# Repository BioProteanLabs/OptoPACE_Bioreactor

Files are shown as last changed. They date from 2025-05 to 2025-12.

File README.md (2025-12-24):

# OptoPACE_Bioreactor

## The OptoPACE Bioreactor (OPB): An Accessible Turbidostat System with Phage-Assisted Continuous Evolution Capability and Optogenetic Controls

## Authors
1. Crane, Ryan D.* 
2. Isaacs, William T.*
3. Ijaz, Manal*
4. Salazar, Nicole
5. Botello, Brianna
6. Kim, Michelle
7. Gonani, Kaeden W.
8. Flores-Mora, Fernando E.
9. Bartelle, Benjamin B.

*co-first

## Abstract:
Continuous culture systems are essential for synthetic biology techniques like Directed Evolution (DE) and Phage-Assisted Continuous Evolution (PACE), which require metabolically active bacterial cultures for extended periods. Turbidostats, which maintain cell density using real-time optical density (OD) feedback, offer ideal conditions for inducing gene expression during mid-log phase, which is the optimal growth stage for synthetic circuit activity. However, current PACE-compatible bioreactors are either cost-prohibitive or require significant technical expertise. Here, we present the OptoPACE Bioreactor (OPB), a low-cost, user-friendly turbidostat system optimized for PACE and optogenetic control. The OPB uses a 650 nm laser and photoresistor to measure turbidity, an Arduino microcontroller for feedback control, and NeoPixel LEDs to enable multispectral optogenetic stimulation. Designed with 3D-printed components and off-the-shelf electronics, the system operates with a single peristaltic pump and uses the siphon effect to simplify fluidics. A custom motor control shield and an LCD-rotary encoder interface enable code-free operation. The OPB supports dual bioreactors connected unidirectionally, ensuring continuous culture while maintaining precise control over optical inputs and nutrient flow. The entire system can be built for under $200, significantly lowering the barrier to entry for labs interested in continuous evolution. By combining affordability, modularity, and ease of use, the OptoPACE Bioreactor provides a robust platform for protein engineering and synthetic biology, enabling broader adoption of advanced continuous evolution methods like PACE.

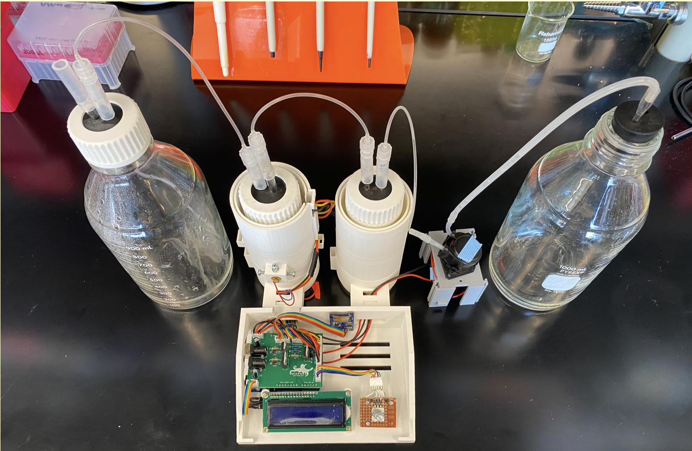
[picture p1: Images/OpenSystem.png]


## Metadata Overview:
Main design files: https://github.com/BioProteanLabs/OptoPACE_Bioreactor/tree/main
Target group: undergraduate researchers, under-resourced laboratories in synthetic biology, students interested in biological hardware
Skills required: 3d printing - easy; software implementation - easy; physical assembly - intermediate; electrical assembly - advanced

Continuous bacterial culture bioreactors are widely employed in biological research, with recent applications in the directed evolution (DE) of biomolecules [1, 3]. In a typical DE experiment, bioreactors  maintain a population of microorganisms in a metabolically active state to support growth and expression of synthetic biological programs. For methods like phage assisted continuous evolution (PACE), two tandem bioreactors are needed: one for growing a substrate culture that feeds into a second “lagoon” to support bacteriophages actively evolving. 
For PACE, maintaining the substrate culture at a steady state gives consistent conditions for DE, requiring either a chemostat or turbidostat control system. Chemostat bioreactors are simpler in that they supply a steady state of nutrients, while a turbidostat makes continual adjustments based on feedback—namely, culture density or turbidity [8, 9, 17]. Turbidostats allow for more optimal and customizable culture conditions but require continual monitoring and control hardware for adjustments based on feedback.
Turbidity is typically measured by optical density (OD), which reflects both light absorption by molecules in the culture, such as pigments, and light scattering from materials with different refractive indexes, typically cell membrane lipids. OD serves as a real-time quantitative assay of cell concentration, allowing researchers to infer the growth stage of the bacterial population. In a bacterial culture, OD measurements typically begin with exponential growth, reach mid-log phase, and eventually flatten out into “death phase” as resources become limited. For the production of recombinant proteins at experimental and industrial scales, mid-log phase is considered the optimal state for inducing protein expression or a synthetic biological program. In a turbidostat bioreactor, continuous monitoring of bacterial growth allows users to identify the mid-log phase, input nutrients to maintain this optimal point, and induce expression of biological circuits.
Induction of biological circuits presents another layer of control required in a bioreactor. Historically, this has meant adding specific sugars or their chemical analog to regulate bacterial operons to initiate expression [2, 16]. This requires an additional chemostat input for the induction agent. More recently, optogenetic circuits—based on biology from plants and cyanobacteria—allow for the induction of gene expression using light. Current developments in synthetic biology have even enabled wavelength-specific optogenetic circuits. With stable culture conditions and multiple biological control inputs, bioreactors could control several genetic circuits simultaneously [4, 10, 11, 14].
Despite their potential, experimental-scale turbidostat bioreactors are not commonly available. The literature indicates that establishing a functional PACE workflow often requires years of effort due to the dual challenges of designing effective synthetic biological circuits and building reliable hardware to support culture [12, 13]. Additional obstacles—such as extensive setup time and the need for frequent maintenance due to microbial biofilm accumulation on culture surfaces—make developing an automated PACE workflow even more difficult to implement.

**The OptoPACE Bioreactor is designed for optogenetic control of synthetic biological circuits.**
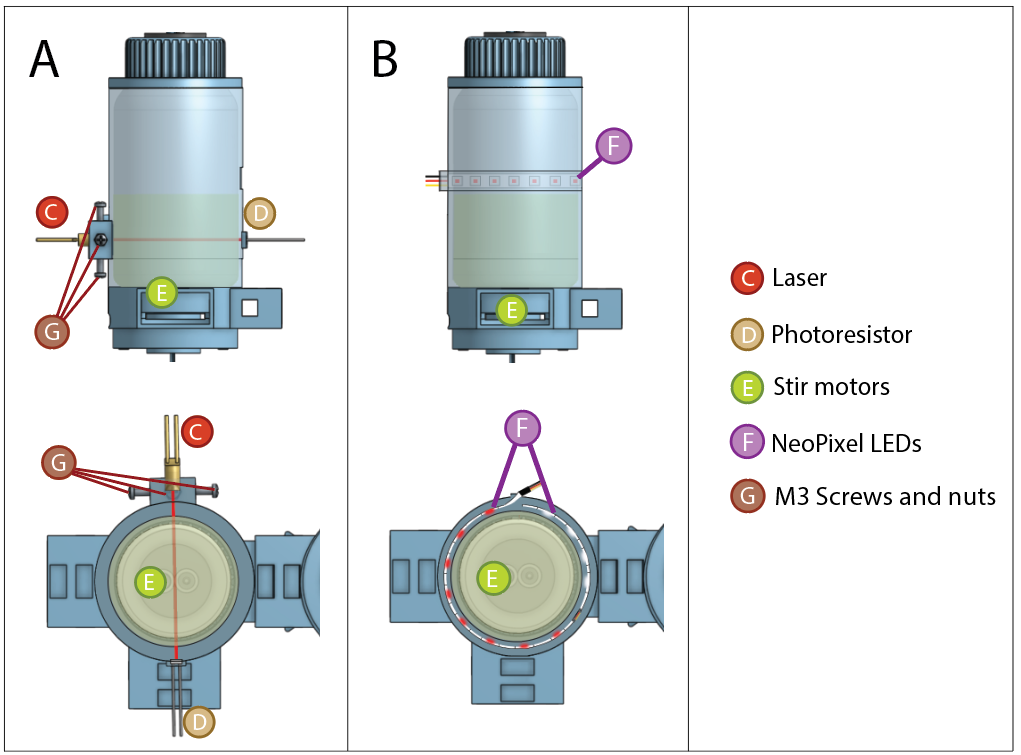
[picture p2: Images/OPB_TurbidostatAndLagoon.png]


**The OptoPACE Bioreactor uses the siphon effect to minimize the number of pumps needed.**

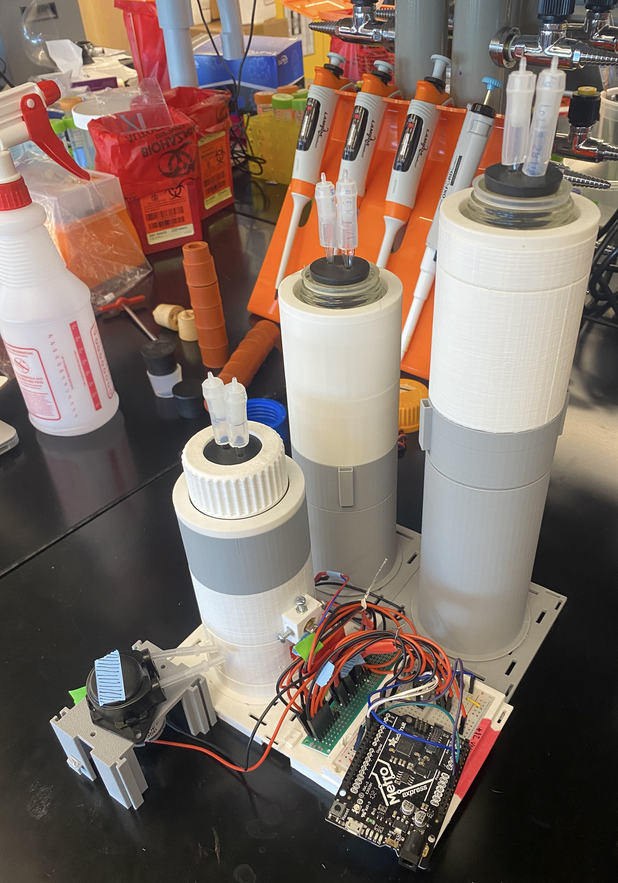
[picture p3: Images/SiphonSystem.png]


**The OptoPACE Bioreactor is controlled by a single Arduino microcontroller and a custom designed motor control shield. It uses a 650nm laser and a photoresistor to measure turbidity, and NeoPixel LEDs for multispectral control.**

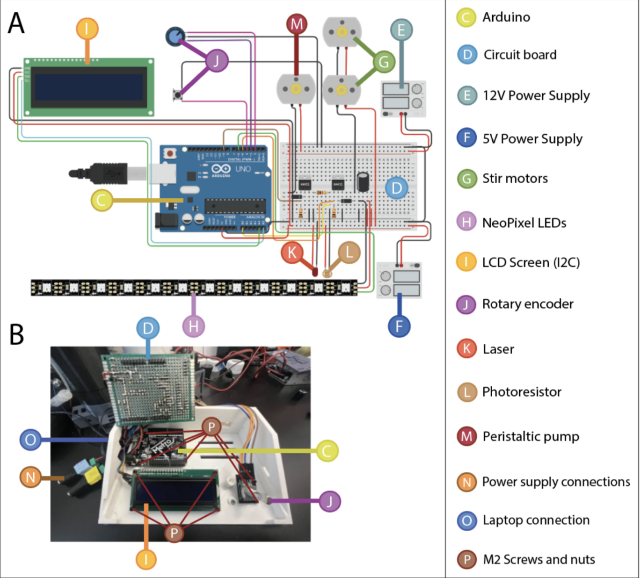
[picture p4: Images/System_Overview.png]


**The OptoPACE Bioreactor uses an LCD screen and rotary encoder as an interface.**
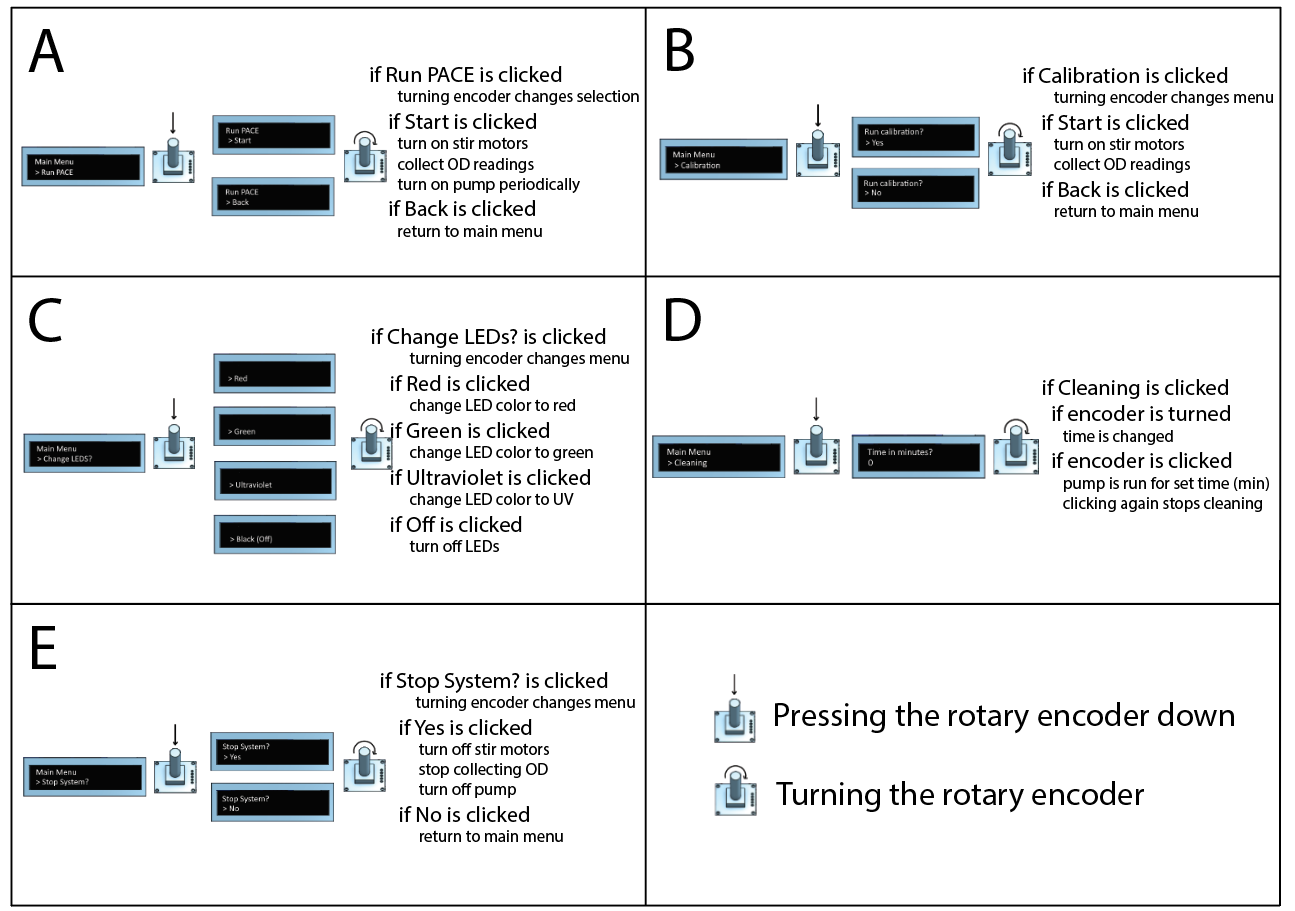
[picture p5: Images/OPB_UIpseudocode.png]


**Turbidity measurements from a 20 hour continuous run.**
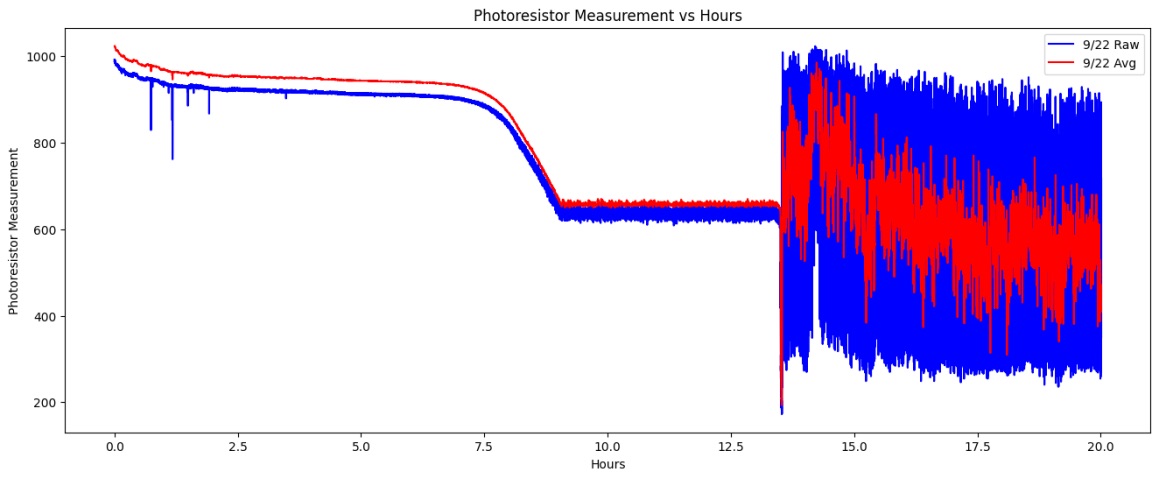
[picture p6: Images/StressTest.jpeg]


 Early measurements required an hour to stabilize before giving consistent readings. Turbidity set point was 650, which was achieved after 9 hours of culture. The turbidostat was maintained for the next 4 hours before the media bottle ran out, giving high noise readings as air bubbles were introduced from the empty line.

## References
[1]	*K. M. Esvelt, J. C. Carlson, and D. R. Liu, “A System for the Continuous Directed Evolution of Biomolecules,” Nature, vol. 472, no. 7344, pp. 499–503, Apr. 2011, doi: 10.1038/nature09929.*

[2]*A. H. Badran and D. R. Liu, “In vivo continuous directed evolution,” Current Opinion in Chemical Biology, vol. 24, pp. 1–10, Feb. 2015, doi: 10.1016/j.cbpa.2014.09.040.*

[3]	*A. Novick and L. Szilard, “Description of the Chemostat,” Science, vol. 112, no. 2920, pp. 715–716, Dec. 1950, doi: 10.1126/science.112.2920.715.* 

[4]	*C. N. Takahashi, A. W. Miller, F. Ekness, M. J. Dunham, and E. Klavins, “A Low Cost, Customizable Turbidostat for Use in Synthetic Circuit Characterization,” ACS Synth Biol, vol. 4, no. 1, pp. 32–38, Jan. 2015, doi: 10.1021/sb500165g.* 

[5]	*A. M. McGeachy, Z. A. Meacham, and N. T. Ingolia, “An Accessible Continuous-Culture Turbidostat for Pooled Analysis of Complex Libraries,” ACS Synth. Biol., vol. 8, no. 4, pp. 844–856, Apr. 2019, doi: 10.1021/acssynbio.8b00529.* 

[6]	*J. De Baets, B. De Paepe, and M. De Mey, “Delaying production with prokaryotic inducible expression systems,” Microb Cell Fact, vol. 23, p. 249, Sept. 2024, doi: 10.1186/s12934-024-02523-w.*

[7]	*T. Sanganeria and B. Bordoni, “Genetics, Inducible Operon,” in StatPearls, Treasure Island (FL): StatPearls Publishing, 2025. Accessed: May 28, 2025. [Online]. Available: http://www.ncbi.nlm.nih.gov/books/NBK564361/* 

[8]	*R. Ohlendorf, R. R. Vidavski, A. Eldar, K. Moffat, and A. Möglich, “From Dusk till Dawn: One-Plasmid Systems for Light-Regulated Gene Expression,” Journal of Molecular Biology, vol. 416, no. 4, pp. 534–542, Mar. 2012, doi: 10.1016/j.jmb.2012.01.001.* 

[9]	*E. J. Olson, L. A. Hartsough, B. P. Landry, R. Shroff, and J. J. Tabor, “Characterizing bacterial gene circuit dynamics with optically programmed gene expression signals,” Nat Methods, vol. 11, no. 4, pp. 449–455, Apr. 2014, doi: 10.1038/nmeth.2884.* 

[10]*P. Ramakrishnan and J. J. Tabor, “Repurposing Synechocystis PCC6803 UirS–UirR as a UV-Violet/Green Photoreversible Transcriptional Regulatory Tool in E. coli,” ACS Synth. Biol., vol. 5, no. 7, pp. 733–740, July 2016, doi: 10.1021/acssynbio.6b00068.*

[11]*L. Forbes, M. Papanatsiou, A. Palombo, J. M. Christie, and A. Amtmann, “Optogenetic control of gene expression in the cyanobacterium Synechococcus sp. PCC 7002,” Front. Bioeng. Biotechnol., vol. 12, Jan. 2025, doi: 10.3389/fbioe.2024.1529022.* 

[12]*S. C. Popa, I. Inamoto, B. W. Thuronyi, and J. A. Shin, “Phage Assisted Continuous Evolution (PACE): A How-to Guide for Directed Evolution,” Nov. 2019, Accessed: Mar. 09, 2020. [Online]. Available: https://www.preprints.org/manuscript/201911.0040/v1*

[13]*S. C. Popa, I. Inamoto, B. W. Thuronyi, and J. A. Shin, “Phage-Assisted Continuous Evolution (PACE): A Guide Focused on Evolving Protein-DNA Interactions,” ACS Omega, vol. 5, no. 42, pp. 26957–26966, Oct. 2020, doi: 10.1021/acsomega.0c03508.* 

[14]*U. Riek, R. Tuerk, T. Wallimann, U. Schlattner, and D. Neumann, “An Automated Home-Built Low-Cost Fermenter Suitable for Large-Scale Bacterial Expression of Proteins in Escherichia Coli,” BioTechniques, vol. 45, no. 2, pp. 187–189, Aug. 2008, doi: 10.2144/000112830.* 

[15]*D. Matteau, V. Baby, S. Pelletier, and S. Rodrigue, “A Small-Volume, Low-Cost, and Versatile Continuous Culture Device,” PLOS ONE, vol. 10, no. 7, p. e0133384, July 2015, doi: 10.1371/journal.pone.0133384.*

[16]*B. G. Wong, C. P. Mancuso, S. Kiriakov, C. J. Bashor, and A. S. Khalil, “Precise, automated control of conditions for high-throughput growth of yeast and bacteria with eVOLVER,” Nat Biotechnol, vol. 36, no. 7, pp. 614–623, Aug. 2018, doi: 10.1038/nbt.4151.*

[17]*Z. J. Heins, C. P. Mancuso, S. Kiriakov, B. G. Wong, C. J. Bashor, and A. S. Khalil, “Designing Automated, High-throughput, Continuous Cell Growth Experiments Using eVOLVER,” J Vis Exp, no. 147, May 2019, doi: 10.3791/59652.* 

[18]*V. Gopalakrishnan et al., “A low-cost, open-source evolutionary bioreactor and its educational use,” Sept. 01, 2022, bioRxiv. doi: 10.1101/729434.*

##
Article: CC-BY 4.0. See: https://creativecommons.org/share-your-work/cclicenses/ 
Hardware: CERN-OHL-P Permissive. See: https://cern-ohl.web.cern.ch 
Software: MIT-0. See: https://opensource.org/license/mit-0

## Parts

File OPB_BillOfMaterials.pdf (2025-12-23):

Cost (total in USD) | Per unit (USD)

Quantity
Required | Link
Pumps:
Peristaltic Pump | 24.95 | 24.95 | 1 https://www.adafruit.com/product/1150

Electronics:
Arduino Uno | 16.99 | 16.99 | 1 https://www.amazon.com/ELEGOO-Board-ATmega328P-ATMEGA16U2-Compliant/dp/B01EWOE0UU/ref=sr_1_2?crid=2BH7CIKCJ7CFA&dib=eyJ2IjoiMSJ9.MazmhFfn-DF8W5oyX_S-tDFAqLRDaMJSkroaZhdQMdisBLxmXEqtvF1FOCIWCK9VmMcdLxz4TK_dkOFiN4Rs4G1MOHO0C2cdoznNzQO9fitpRigfG_jyAHAxld8StKFz9U3h0JzKR6nlSri_QrVfRveh9TLyUJtKpQYNyRvr7e_Mk90qR3Vuww9b6Qn0lZH-mpveGqZg1Tc_CPVMISl0SIQF9eqJeR12jGkVYwXVRCChSu2XjLfS69RXut5ycPQBIdoHiU0czHEM2wM81zCh5hcre4O_QuutMAEhb_OEpfc.n_AJTySz6zBJVmoDv2wWDHNbWEV4MwIe4viY1KqEE1s&dib_tag=se&keywords=arduino+uno&qid=1727481167&s=industrial&sprefix=arduino+uno%2Cindustrial%2C129&sr=1-2
DC Motors | 6.99 | 1.7475 | 2 https://www.amazon.com/BOJACK-Pcs-Type-130-EK1450/dp/B09FPXF1QK/ref=sr_1_5?crid=SYDPQHVU1UCJ&dib=eyJ2IjoiMSJ9.ZvsO9y9VV2Cti8BPB2elIcQrtpUiZfOZ90OiEF3u8S2JqaXfD8roBZbpWuHwGUnWUJrtgxDCdDbqlT062z_vzXDY4UDEtTG2QOMZvhHwkoVGQaoRdqJQJRGFWIuxLYeunvejxsyGBOZgrbz7kBY9varfIFxPFtSZM_t88NIoVAv9nuIoEJbI5mnzILcSL-YL2eq_LeHGlcL8qbhE7fut4_CdGq03AfdYGX6FPTGZ8sx3kr_MgYbUSgLNgBAUdTIr1PRMZQJKwQBsy-QLFd201Fft08rG1EnqHYplswOcBfA.tpAMfRI84GYtpn5l6mxYFQuOmqMq7r5aFAcDlF5maa0&dib_tag=se&keywords=dc+motor+arduino&qid=1727489473&sprefix=dc+motor+arduino%2Caps%2C138&sr=8-5
Magnet for Stir Bar | 1.5 | 0.75 | 2 https://www.kjmagnetics.com/proddetail.asp?prod=B22C
Neo Pixel RGB Strip (1
meter) | 16.95 | 4.97 | 1 https://www.adafruit.com/product/1426?gad_source=1&gclid=Cj0KCQjwsuSzBhCLARIsAIcdLm7B5-E9eEBKmAclRtZ55TevoP9Ts5JCG6-ikKHFX-0JpmEfh3KP4hUaAuzuEALw_wcB
Neo Pixel UV Strip (1
meter) | 19.95 | 4.92 | 1 https://www.adafruit.com/product/3851?gad_source=1&gclid=Cj0KCQjwsuSzBhCLARIsAIcdLm7sCD9aQWDhDVkyhXy79CN7jM51O9Vu0E5j3pv7IjfmdTo9FJND3uEaAuvcEALw_wcB
Capacitor | 6.99 | 0.466 | 1 https://www.amazon.com/ALLECIN-Electrolytic-Capacitor-0-2x0-43in-Capacitors/dp/B0CMQBXG8W/ref=sr_1_1_sspa?crid=2P6FQCTPPZET1&dib=eyJ2IjoiMSJ9.EeRzVxgbry73PU81OfEdUTHHxefg7__akg6enD1ug2QqvUMahZM0egv24Ncmgsr6QNtSmHqpcjtyXPLhjQ04OR9VbHoEDxix56ssPrgHx8krXzxMMxhvY6eJbWf1SYPKSs3Mp_k5pNcwe7tIE1zYPnX0hH0U6DMaMaYMbpqlf_Az75BOFh7WiRFcDC9D44D6rOJ_BwdmqKI-1jNOrCrLl_U50FppxQuiJycx_DZ-swbkCzMISijJE0fuztHdx1gDlNp8sfdWhomQoorPCO5IszvSVfTQ3bjOfbIuHtV4YJ8.klcSA6D7Z0aH6rdgYZ4UTe1-_liNX5hCePJDdrTr87Y&dib_tag=se&keywords=capacitor&qid=1727487022&s=industrial&sprefix=capacitor%2Cindustrial%2C137&sr=1-1-spons&sp_csd=d2lkZ2V0TmFtZT1zcF9hdGY&psc=1
Diodes | 5.99 | 0.04 | 2 https://www.amazon.com/ALLECIN-FR207-Recovery-Rectifier-Switching/dp/B0CKSQCPMF/ref=sr_1_1_sspa?crid=27SUBKZNOQKSR&dib=eyJ2IjoiMSJ9.nF0zX9l8qQBCowDIJePKKqbGrzIoOo3PNJax72tZ6qjg9kgmgw81jC3aYIDwfXFTW6xrn6SgkQCsQHqSbGLn5_9nvPEX7atNdrpCw0V4KPMw_xORMTTsCoKXGB8LbGoxTHEQBNe47z8oBwsXCIFj-Q_xcAZYFQlxgAZw-x6lBlCdUeJaQ3o65ilHOWPbDFyAi-yEhBERUdksS2dtLqOy4PH8HyeqJHflh9ZPmTTQ-Zo.RyWDcqhPzG723PAy93r8O3BZAwdo5a78Xj-lMl3S8rk&dib_tag=se&keywords=diode&qid=1727489768&sprefix=diode%2Caps%2C144&sr=8-1-spons&sp_csd=d2lkZ2V0TmFtZT1zcF9hdGY&psc=1
N Channel Mosfet | 8.99 | 0.9 | 2 https://www.amazon.com/Bridgold-IRLB8721PBF-IRLB8721-Channel-Transistor/dp/B07LG5BCDY
Resistors | 7.99 | 0.015 | 3 https://www.amazon.com/Elegoo-Values-Resistor-Assortment-Compliant/dp/B072BL2VX1/ref=sr_1_6?crid=PDM69LSMUIY9&dib=eyJ2IjoiMSJ9.tcSxr7hPPqdB-rRLfuwuE21RnA76nhklyN7bzrqSMgFQtziCqUX0AX6MJRLwkC37duP6w9DOmNmGzP5QygbkrX5c1ApZmxSG5nklQscxRZx4bxBueyZ8fvKK1DtlQdKVia8zXnAX4VmNssQjlc2XVEbU-r7naUFVEOyD8kFdsLWMItc8PNwLvt6LEAuM0a_y2Qrccmak8wmR7c0OK4CEavClhlb1eF7VlJ_GAOJE2XI.TGzCfT094J-d-iQj16elvor_x5r7DpaTk-ppVHwYkLU&dib_tag=se&keywords=resistors&qid=1719530730&sprefix=resistors%2Caps%2C166&sr=8-6
5V/12V Power Supply
(and Cord) | 20.98 | 20.98 | 1 https://www.amazon.com/Arcity-Switching-Adjustable-Machine-Cocktail/dp/B07X1LBK19/ref=sr_1_3?crid=R58V1N6WU06H&dib=eyJ2IjoiMSJ9.fJm0gL2tFYHpLtpl2ZvtcmxHyLCi-xgmObd8YQG8b6KbXz0gZs_tAIOS3cCaO--AQLrJHBaOjwobY-q8sFawsXHw68pAIAi4_ECzUJUuFqBmoq0MTd1EuS-fnSulPfOR7Mm97oxBMzDioSOEHIRLkDWZEd6hlsUjZbgglq9yTextep1qgT8981E6IQeIhgL_vPSdcCxM5Ozn6QI_Qqoatj6nPgDcyA8XMMPFIs_3K6M.mMvoNo5uI9WSPrp6b4Q2HwEDbKeB7vZfMG2JrGZ3u6M&dib_tag=se&keywords=12v+and+5v+power+supply&qid=1727490277&sprefix=12v+and+5v%2Caps%2C177&sr=8-3 (https://www.amazon.com/dp/B00M8TBJLK?s=industrial&sp_csd=d2lkZ2V0TmFtZT1zcF9kZXRhaWw)
Connectors/Crimps | 12.99 | 0.02 | 50 https://www.amazon.com/IWISS-Connectors-Connector-Electronic-Diagonal/dp/B07QGBKFYZ
Wire | 9.98 | 0.2 | 10 https://www.amazon.com/BNTECHGO-Silicone-Flexible-Stranded-Impedance/dp/B01K4RP9UE/ref=asc_df_B01K4RP9UE/?tag=hyprod-20&linkCode=df0&hvadid=693128203619&hvpos=&hvnetw=g&hvrand=8621537138776061854&hvpone=&hvptwo=&hvqmt=&hvdev=c&hvdvcmdl=&hvlocint=&hvlocphy=9030087&hvtargid=pla-593184646218&psc=1&mcid=899ae3c599a936a7a7f2892123133321&gad_source=1
Shrink wrap tubing | 24.99 | 0.25 | 1 https://www.amazon.com/WORKPRO-100FT-Heat-Shrink-Tubing/dp/B0C4Y4BD9J/ref=sr_1_6?crid=2BQOT6X4V82JA&dib=eyJ2IjoiMSJ9.-da4vAIagdBQEVX2YOz6k-vvv7_TwLZsDgpWuC39UW3bl5gqUOOgSs_URKe2-b_0bTSROdXHCuQtK4cmtgtrZ1U5XPP4pC0JZ3OcI7cWZSTH7oVQfj3gH0F7tMlA_6DtY48GD8f3gVq3QVZc4v2Yzd_KrFfLslBu3fIlgfCgEh4-EIJPgvY9VQAuo0isIvTOlgay0bBOYGw9tGYeTIJzKhOGEQtnmzX9W55NsHZ2wvA_uaI0mkMp6h8eDtJXrMbr3JckzaizkYKimhiTna1d18yDrHRsIL0u_0Rd5jk3iQk.CcfQkwjQWDeGzpm6v9UbrfGzm5Q6U8sawAkwuHGUNlw&dib_tag=se&keywords=shrink%2Bwrap%2Btubing%2Braychem&qid=1719530592&s=industrial&sprefix=shrink%2Bwrap%2Btubing%2Braychem%2Cindustrial%2C135&sr=1-6&th=1
Proto board | 9.99 | 0.31 | 1 https://www.amazon.com/ELEGOO-Prototype-Soldering-Compatible-Arduino/dp/B072Z7Y19F/ref=sr_1_1_sspa?crid=1X9C6Y1FI3PXX&dib=eyJ2IjoiMSJ9.aAkey0GxSdsBlIR3vNq8qpkkTSdXkwHRkdq9eKcPyWYJJHH-BWtDJLHyDjo44N1GbMaEKYO4hjSdUtSisLE6JC2eglVfWtd9Rlhz6Qc1CQm4JB82u5or0VRAHQ0ZWcbooZBmTO2q5kRC4OA_jX9pG2tHdOX_ZTXiU2LbCFpHw9xAQmrR3T3_BTUepHQWHwvBZ7_MSCfynABUg3ErTQXFKVWH7rbm0pPGUuxSMAjcoZCnQwlBEkb6me4RE3Ym5G_DzT6b0psptMsBeBAfK7bXtGLCThfFiDrlYfvCnWzExmg.dVgCC9FM987FqwcdPlqMRWGuwCfbXTDyFyZ3mNY9aiI&dib_tag=se&keywords=protoboard&qid=1719529796&s=industrial&sprefix=protoboar%2Cindustrial%2C112&sr=1-1-spons&sp_csd=d2lkZ2V0TmFtZT1zcF9hdGY&psc=1
header pins | 12.75 | 0.11 | 35 https://www.amazon.com/Glarks-Straight-Connector-Assortment-Prototype/dp/B076GZXW3Z/ref=sxin_16_pa_sp_search_thematic_sspa?content-id=amzn1.sym.140400a7-1208-46ad-8d2a-eb6e8eac81b5%3Aamzn1.sym.140400a7-1208-46ad-8d2a-eb6e8eac81b5&crid=3L1XUEITBAFQI&cv_ct_cx=header+pin&dib=eyJ2IjoiMSJ9.GgFpttt2kd6M2wlWPgYVNcxR9u_Z54BD9LquaYNCrjeWDxcw_JWzaNC6nmrmfz9QNCD6TtmEDkPe-VjmMr0fbg.wf5JieKtfx0eRQ0kaXJknpJ_0QnVjAYxNhVqALqlquA&dib_tag=se&keywords=header+pin&pd_rd_i=B076GZXW3Z&pd_rd_r=8836237b-88ef-44fb-a1cb-6fb5975885ce&pd_rd_w=xxmPa&pd_rd_wg=ATzcS&pf_rd_p=140400a7-1208-46ad-8d2a-eb6e8eac81b5&pf_rd_r=MNZ3QN9V4PRHSNWYHNAT&qid=1727472053&sbo=RZvfv%2F%2FHxDF%2BO5021pAnSA%3D%3D&sprefix=header+pin%2Caps%2C147&sr=1-1-6024b2a3-78e4-4fed-8fed-e1613be3bcce-spons&sp_csd=d2lkZ2V0TmFtZT1zcF9zZWFyY2hfdGhlbWF0aWM&psc=1 Data/power cable (for
arduino) | 6.99 | 3.5 | 1 https://www.amazon.com/DIYmall-Cable-Arduino-2560-Pack/dp/B09JRXT1TY/ref=sr_1_1?crid=FI0WZEHVYC85&dib=eyJ2IjoiMSJ9.5rjOB-LdqEHvWd5xxe8wc-g8r-To8tfftnwEWf5fVUCOohXvTtGthn9NlC82gNfFj7nLrsSVdk-wqdt_4C_dlfAC9qzrFcX5yPN1NNqy-lP6n_5irUaU_YSww8e6t6nVkrlMfy2SnXmgX4tBd96QBOU5LsxgS6TkPyUawUgIJHZ8sxUjAvxA9mlXN_haIdJQK9KycxRXvUOVTbwuM82vH9QWmhlSAvWLtluXZYIXJ48.pQ_IMxu2tL4iQiNUP2TalJIqkUSVC0mx5L7EyvPNW2A&dib_tag=se&keywords=arduino+usb+a+to+usb+b&qid=1727471932&sprefix=arduino+usb+a+to+usb+b%2Caps%2C159&sr=8-1
Laser (10 pack) | 6.79 | 0.679 | 1 https://www.amazon.com/HiLetgo-10pcs-650nm-Diode-Laser/dp/B071FT9HSV/ref=asc_df_B071FT9HSV/?tag=hyprod-20&linkCode=df0&hvadid=693675076785&hvpos=&hvnetw=g&hvrand=11377644762616819857&hvpone=&hvptwo=&hvqmt=&hvdev=c&hvdvcmdl=&hvlocint=&hvlocphy=9030087&hvtargid=pla-1648419633338&psc=1&mcid=99588c8c304a356cb28d4d1895770f83&gad_source=1
Photoresistor | 14.89 | 0.07 | 1 https://www.amazon.com/Glarks-Photoresistor-Sensitive-Dependent-Assortment/dp/B08K2GZYN9/ref=sr_1_3?crid=1EIUJTEA3D2HH&dib=eyJ2IjoiMSJ9.bvyCzg0AJWIW8dHSwCcqCyOqC2wx8CoL-yMZ-WXNY4Cv67Ptt0ujitf4NfMFj7Ptb63sT_9MtaAi3itULXeR0Luf2kLA5y8hJeUjsTjsticViQ5xBCANXSiHHz0sKL3VBKnfZ5bOLm2vDv3O4NRg2_GDQXojFdkKyjjdcTf5KZpT9926ozJKzqqFvpcHs7mGAPaNv-PywAJsBJRAE_hOQpWGLydSPo8iBWCM3gcyV_bmQ61Owyh0mIcRMB1Tvx8XpsEi-NnsMks9l2fIftWgQFTmw36-vOOVl83dF2zb7-M.Qh3K4kQTZbMuaLB6eEdbHwyO6h5V8vvOW8c6g6sUfdA&dib_tag=se&keywords=photoresistor+glarks&qid=1719530872&s=industrial&sprefix=photoresistor+glarks%2Cindustrial%2C120&sr=1-3

Tubing/connections/Sto
ppers:
1mm id tubing | 5.49 | 0.07 | 18 https://www.amazon.com/dp/B07PPWNJSM?ref=ppx_yo2ov_dt_b_product_details&th=1
Pasteur Pipettes | 40.61 | 0.2 | 4 https://www.amazon.com/CHEM-SCIENCE-INC-123-403-02-Borosilicate/dp/B07C81BSBC/ref=sr_1_2?crid=KAZNNARQMPVG&dib=eyJ2IjoiMSJ9.0fJSv_rL7_egEjnk61NunY_YCHODvT4p2C0uSv4qQJoKQLM7WnbtwwzxDd1FpZ4L3hrwAa40pR7D3aHl_d3w-_ct-iSKvF7ouHMBFR2KETJAiXcuVEZsBFFO6euFghbzGLfyIAcQZq8Ukpd02ts_oKpMpA65ldjUyEGFMREmoD3f7r4PYcUeJ3PISqRcAITzHYpMCpQCbaGqC-YqSZnQP5g_hYN713k3PSWbQJ8hDP7UV-IakoIZumr5_Dn8Cm8JYKVoD_uzyu5DwOp-Af9GhfWGhaKujkIKeJkyqZuBW7c.yxYO8Bd6LBxjasdojx6w76uaKwdXlXZQLbmtkPKno1w&dib_tag=se&keywords=pasteur+pipettes+glass&qid=1727480647&s=industrial&sprefix=pasteur+pipettes+glass%2Cindustrial%2C133&sr=1-2 Large diameter tubing for
pipette connection | 7.99 | 2.44 | 2 https://www.amazon.com/Quickun-Silicone-Brewing-Kegerator-Aquaponics/dp/B08JQPZ4H4/ref=sr_1_1_sspa?crid=3IUVS87MFPM2M&dib=eyJ2IjoiMSJ9.5DbywonMYQA_SNup0fJIX0gOdmyZAfv8-Jm4q0JbkUtth9oYzd0mjPw0-EySPTYkPA_wRKU4gq8T3uaEyOc9DI_bE7u885IeSbUn2AU2JJDUucEY8b8xD0D9qzqx1_FnRMg0KCdVhOn5epVhGEgDxhjPImd8cYQA8dD7U_xayRXao8_arnreGsGAqm9DsS_zC9rYk9fIZc94yjpwKgY2WtLOfxjHaQLjPlu74ZCX7H4.BNXEC6t4tudJElDFXjxSYcUqYFQj-Kbpm-bDBcWA4DQ&dib_tag=se&keywords=4mm%2Bdiameter%2Btubing&qid=1727488352&sprefix=4mm%2Bdiameter%2Btubing%2Caps%2C125&sr=8-1-spons&sp_csd=d2lkZ2V0TmFtZT1zcF9hdGY&th=1
Rubber stoppers (4 count) | 5.28 | 1.32 | 4 https://www.widgetco.com/products/6-rubber-stoppers-with-2-holes?variant=36844381110433&tw_source=google&tw_adid=&tw_campaign=19746625393&gad_source=1&gclid=CjwKCAjw65-zBhBkEiwAjrqRMCAYFGBJAlqpS33Dan3j3EDJ1aCqn2h9nFcXqikCzBAler03LXvl9xoCmgIQAvD_BwE
3d Printing Filament | 25.99 | 15.6 Roughly 600g | https://www.amazon.com/HATCHBOX-3D-Filament-Dimensional-Accuracy/dp/B00J0GMMP6/ref=asc_df_B00J0GMMP6/?tag=hyprod-20&linkCode=df0&hvadid=692875362841&hvpos=&hvnetw=g&hvrand=6607874986992330473&hvpone=&hvptwo=&hvqmt=&hvdev=c&hvdvcmdl=&hvlocint=&hvlocphy=9030087&hvtargid=pla-2281435183818&psc=1&mcid=08d6151a54cd3148a9c51100f1fac85d&hvocijid=6607874986992330473-B00J0GMMP6-&hvexpln=73&gad_source=1
Female 1/16" Luer lock
connector | 8.99 | 0.3 | 6 https://www.amazon.com/Syringe-Adapter-Clear-Female-Luer-Connector-Kit-Coupler/dp/B0BM9QPS3M/ref=sr_1_5?crid=3R77DF3H2BXXQ&dib=eyJ2IjoiMSJ9.J-cO4Xab9T0VmeSBwKWJqzfva77VMFkFN83_1zp2dbTgxGuPcPpJB4fIW9snjuoLvZld2Pc27cJzWPON7tujv9vaZYFQemhM4UcoDLsGRgmARzWWIXpbYdVC6lLF_41c3livs0Azs9Ne2VHKEADBlX3qkTkMbErxiOS6_XPckoZ8VMd9pbZwLzyuv-0Mqy_zRn6aequI6F6ajUY4GDf6RzA2pSGcJHKX5D78kOfIwjQUzb_LNLjcU-lTCez-YubCLbqJizi8vl_MwlfcVqw-5uZUpvOUoqC8NAAF2869xLU.3DPzVYx1qLxN7CoAArZ0fVQzFHaSUjDxpI06bCr-Y8o&dib_tag=se&keywords=Luer+lock+connectors+1%2F16+to+1%2F4&qid=1727728107&s=industrial&sprefix=luer+lock+connectors+1%2F16+to+1%2F4+%2Cindustrial%2C126&sr=1-5

Male 1/4" Luer lock
connector | 7.99 | 0.27 | 6 https://www.amazon.com/30pcs-Syringe-Adapter-Connector-Coupler/dp/B0BVZ9W33R/ref=sr_1_6?crid=3R77DF3H2BXXQ&dib=eyJ2IjoiMSJ9.J-cO4Xab9T0VmeSBwKWJqzfva77VMFkFN83_1zp2dbTgxGuPcPpJB4fIW9snjuoLvZld2Pc27cJzWPON7tujv9vaZYFQemhM4UcoDLsGRgmARzWWIXpbYdVC6lLF_41c3livs0Azs9Ne2VHKEADBlX3qkTkMbErxiOS6_XPckoZ8VMd9pbZwLzyuv-0Mqy_zRn6aequI6F6ajUY4GDf6RzA2pSGcJHKX5D78kOfIwjQUzb_LNLjcU-lTCez-YubCLbqJizi8vl_MwlfcVqw-5uZUpvOUoqC8NAAF2869xLU.3DPzVYx1qLxN7CoAArZ0fVQzFHaSUjDxpI06bCr-Y8o&dib_tag=se&keywords=Luer+lock+connectors+1%2F16+to+1%2F4&qid=1727728107&s=industrial&sprefix=luer+lock+connectors+1%2F16+to+1%2F4+%2Cindustrial%2C126&sr=1-6 Other
M3 bolts | 0.92 | 0.23 | 4 https://www.amazon.com/VKKM-Stainless-Assortment-Reusable-Adjustable/dp/B0CL14BWNC/ref=sr_1_1_sspa?crid=1HB5DNP6IDORH&dib=eyJ2IjoiMSJ9.P_MOBrskKLS2bpPXZVnpjOZ5dU3FLr5E12S0vV0z8Rpj-wSCRjTmE95qJy5xXgBwnIiGARswPmiFAGprjfdwxf_FZzj_xSvpLq-2pQ1_-5WOORO0uJahj6Ja8W-TUDDB_BW0Tgk5sm5eakwrjmtGT5uNnhtEy3xyOqodXmjLq5wb7s1cs329e_NBJq2FQaEwx8OvY11pdPxUnsmT7W6Pm5eF_Vgyu-OjJpsLuKqvY3m0JLpIbCgU4yGrtBFrjJfwGRfzokPQa0LMQLNybIkckgZuMLVlCw1lL9225tYX118.20aAKDRZIPPAegQ9LTElWe8JQXLFJDSqWpbLvmzcthY&dib_tag=se&keywords=m3+bolts&qid=1727487154&s=industrial&sprefix=m3+bolt%2Cindustrial%2C164&sr=1-1-spons&sp_csd=d2lkZ2V0TmFtZT1zcF9hdGY&psc=1
M3 Nuts | 0.6 | 0.15 | 4 https://www.amazon.com/VKKM-Stainless-Assortment-Reusable-Adjustable/dp/B0CL14BWNC/ref=sr_1_1_sspa?crid=1HB5DNP6IDORH&dib=eyJ2IjoiMSJ9.P_MOBrskKLS2bpPXZVnpjOZ5dU3FLr5E12S0vV0z8Rpj-wSCRjTmE95qJy5xXgBwnIiGARswPmiFAGprjfdwxf_FZzj_xSvpLq-2pQ1_-5WOORO0uJahj6Ja8W-TUDDB_BW0Tgk5sm5eakwrjmtGT5uNnhtEy3xyOqodXmjLq5wb7s1cs329e_NBJq2FQaEwx8OvY11pdPxUnsmT7W6Pm5eF_Vgyu-OjJpsLuKqvY3m0JLpIbCgU4yGrtBFrjJfwGRfzokPQa0LMQLNybIkckgZuMLVlCw1lL9225tYX118.20aAKDRZIPPAegQ9LTElWe8JQXLFJDSqWpbLvmzcthY&dib_tag=se&keywords=m3+bolts&qid=1727487154&s=industrial&sprefix=m3+bolt%2Cindustrial%2C164&sr=1-1-spons&sp_csd=d2lkZ2V0TmFtZT1zcF9hdGY&psc=1
M2 bolts | 8.99 | 0.011 | 12 https://www.amazon.com/600pcs-Premium-Socket-Assortment-Washers/dp/B0D2KWKX5S/ref=sr_1_3?dib=eyJ2IjoiMSJ9.SIpxbAcz3Eys5szxflwamvlV8-nOtf9r1fw7xtpGaZtOit5XPPGKNQZr_PZaEUieEjM2FBAev-DuU0agdeSvZIYxFt7XY6oTOPPjkrAtgeTKmXr1y0tUStPPnjAsMLKGFh_4q11KdSKvq_RV3PrzER2d0RmfMl1tXAMlNl8_MmSsWdCrb1vKsQHe02BDNkz6bB6mJaoJ7Ab-yHHKpYr2pFeRYRIF_qHJcqyoJ36HdvOgfS6AGsMQfpXwI2ZqrYOTKVcXKoa2NWko_T2plm6W2BbDBxKrtWNbF1AwTsyTVyk.Seih0Ug3GEjsAVua4l3vwUiEMrrfVA8QExi9tDWQmLY&dib_tag=se&keywords=m2%2Bbolts&qid=1727488121&s=industrial&sr=1-3&th=1
M2 nuts | 8.99 | 0.011 | 12 https://www.amazon.com/600pcs-Premium-Socket-Assortment-Washers/dp/B0D2KWKX5S/ref=sr_1_3?dib=eyJ2IjoiMSJ9.SIpxbAcz3Eys5szxflwamvlV8-nOtf9r1fw7xtpGaZtOit5XPPGKNQZr_PZaEUieEjM2FBAev-DuU0agdeSvZIYxFt7XY6oTOPPjkrAtgeTKmXr1y0tUStPPnjAsMLKGFh_4q11KdSKvq_RV3PrzER2d0RmfMl1tXAMlNl8_MmSsWdCrb1vKsQHe02BDNkz6bB6mJaoJ7Ab-yHHKpYr2pFeRYRIF_qHJcqyoJ36HdvOgfS6AGsMQfpXwI2ZqrYOTKVcXKoa2NWko_T2plm6W2BbDBxKrtWNbF1AwTsyTVyk.Seih0Ug3GEjsAVua4l3vwUiEMrrfVA8QExi9tDWQmLY&dib_tag=se&keywords=m2%2Bbolts&qid=1727488121&s=industrial&sr=1-3&th=1

Optional Components

SD card Module | 6.99 | 1.4 | 1 https://www.amazon.com/HiLetgo-Adater-Interface-Conversion-Arduino/dp/B07BJ2P6X6/ref=sr_1_1?dib=eyJ2IjoiMSJ9.tv7rM_vKO1Fape29lticl_Je0sYt7aIDk-kT5tsqB1DhdzWf_Px_nsU_u0o-pCEj53-AQ8q7X5BCrKdvYJPiwVp6uqIgCPIXdT5FJpud2S0kBuUFCS4zKO-fOP3KNjVFqLyk1hWBfNro-wNLl5_GiLhnppJZrGwO-ZnByz5r7IFNJfeMFM7bJtM92Bt4aCYHvaDSUgDJe-Rigntj45Dv44nRUm1r7L9qrykx_B7-prI.89wR7aVP5kASXpnukbtVnFG4DxhWPYmIdUMVpaE5z1s&dib_tag=se&keywords=micro+sd+card+arduino&qid=1727482883&sr=8-1
LCD Screen | 10.99 | 10.99 | 1 https://www.amazon.com/dp/B07S7PJYM6?ref=cm_sw_r_cp_ud_dp_GRWSHQ1DEDV7H11BQKK5&ref_=cm_sw_r_cp_ud_dp_GRWSHQ1DEDV7H11BQKK5&social_share=cm_sw_r_cp_ud_dp_GRWSHQ1DEDV7H11BQKK5&skipTwisterOG=1 (https://www.amazon.com/dp/B07S7PJYM6?skipTwisterOG=1)
Rotary Encoder | 8.89 | 1.78 | 1 https://www.amazon.com/Cylewet-Encoder-Digital-Potentiometer-Arduino/dp/B07DM2YMT4/ref=sr_1_3?crid=3MTO3GWPS24N6&dib=eyJ2IjoiMSJ9.561HXmjsvo5F8O9BqiyjaWUXK69kOQKbJud4m1ldFVWyJKNxRnZAhSLPpVmuRi3mw_fNGnOcfvuXT2DGNs9av8pc_o8IlBtxdsxxqxaVK3uMDo4WeZHdwN0MdXjTRKe-9496roiEi_lSF79iHzpCn6ZfshcVHZ2vPU7m8JTO2oaG1VkLcZ39wUMOHosfxjHKqy8H8MpHpoIoHc_B9PNFZcIQeN0DawA2fWOntWR-DFv6TfwsKqy2z5RukS1WOEa4_eKoXCdrmHN89LHawHTzXwEKCjEJF5GczWl1dwUtk-Q.o3EKeHdjZD-BR-CxM2Se98Cn1N0JuUHjAtSwLWbnyBQ&dib_tag=se&keywords=rotary+encoder&qid=1727482750&s=industrial&sprefix=rotary+encoder%2Cindustrial%2C137&sr=1-3
Net Total: | 386.35 Actual Total: | | 123.449

Assumptions:
Access to a 3d printer
Access to tools to crimp wires for connections Ability to cut glass pipettes
Access to soldering iron and solder
Access to wire cutters/strippers
Access to heat gun to shrink shrink wrap
Access to incubator
Access to sterilization, either chemical or autoclave Access to glassware and stir bar
Some form of adhesive ideally superglue
Access to laptop

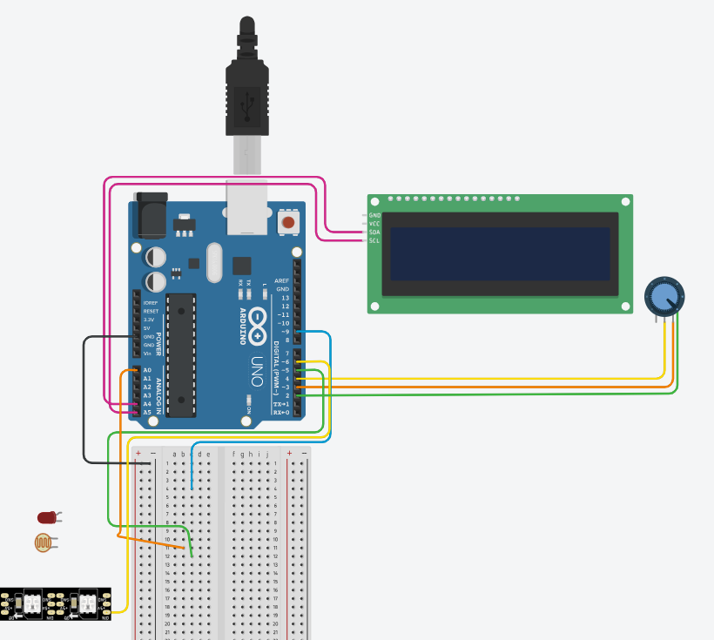
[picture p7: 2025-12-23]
Images/Parts connected to microcontroller - Schematic.png

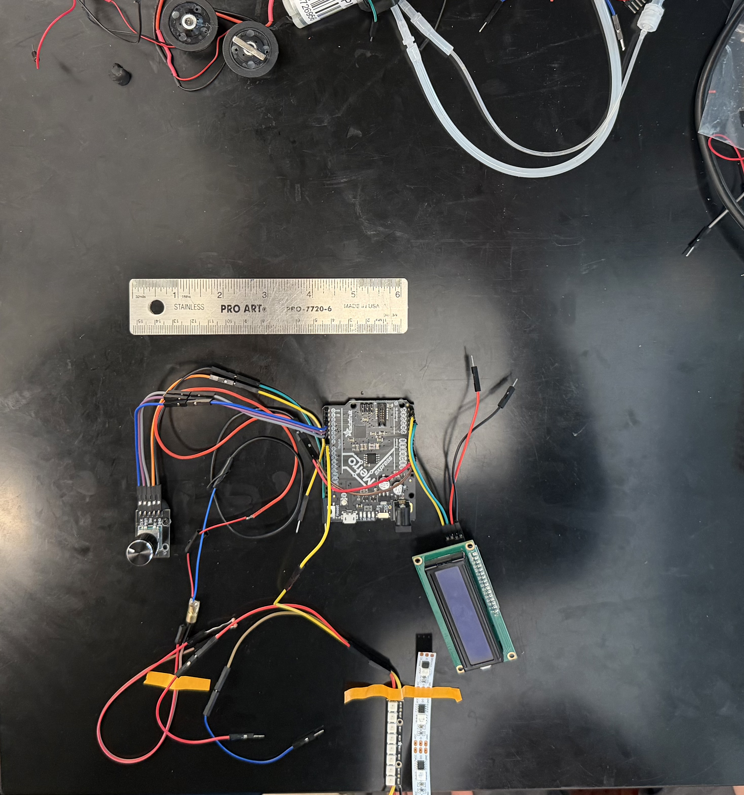
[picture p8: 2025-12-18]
Images/Parts connected to microcontroller [not shown in assembly].jpeg

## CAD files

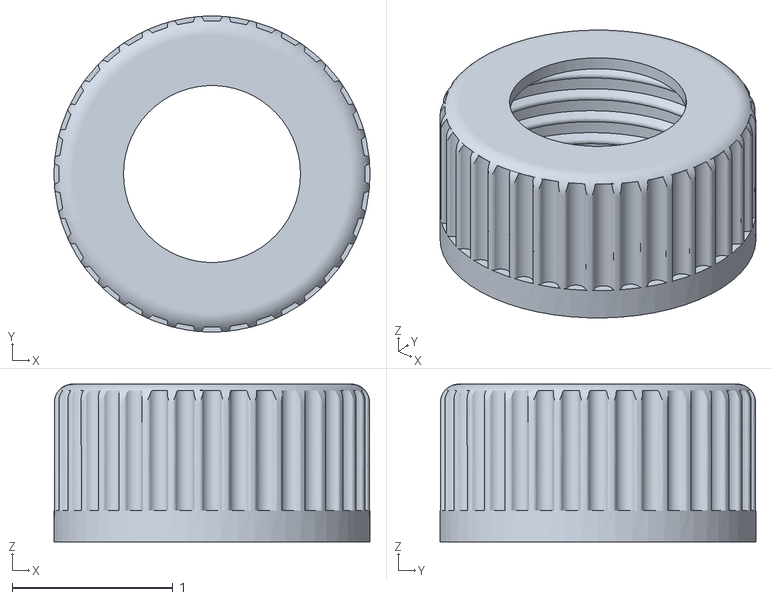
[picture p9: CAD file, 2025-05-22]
CAD_Files/inches/Custom Cap for 100ml bottle (in).stl
1.97 x 1.97 x 0.984

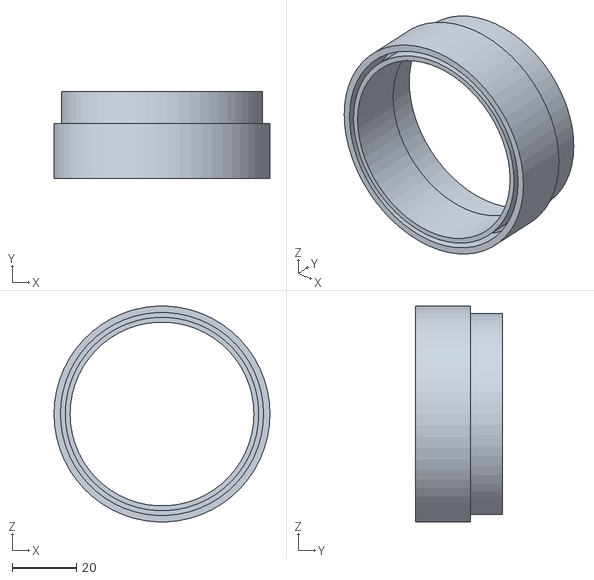
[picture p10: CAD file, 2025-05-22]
CAD_Files/millimeters/Intermediate Base Segment (mm).stl
67.0 x 27.0 x 66.9

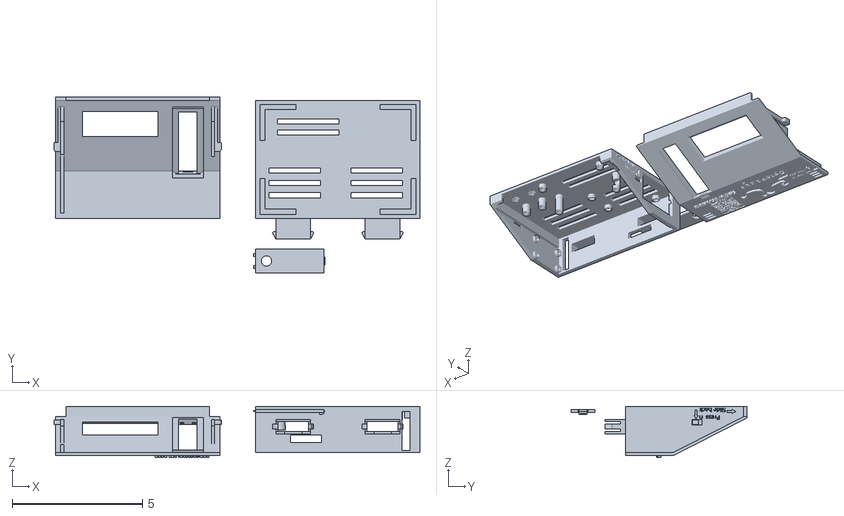
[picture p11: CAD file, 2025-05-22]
CAD_Files/inches/Control Unit with Lid (in).stl
14.0 x 6.73 x 1.97

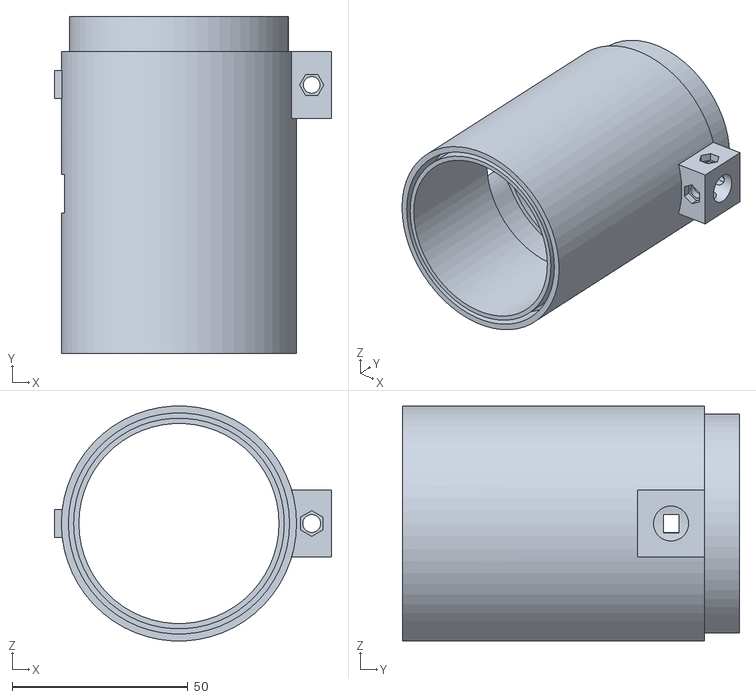
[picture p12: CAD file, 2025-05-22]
CAD_Files/millimeters/Turbidostat Segment (mm).stl
79.0 x 96.0 x 66.9

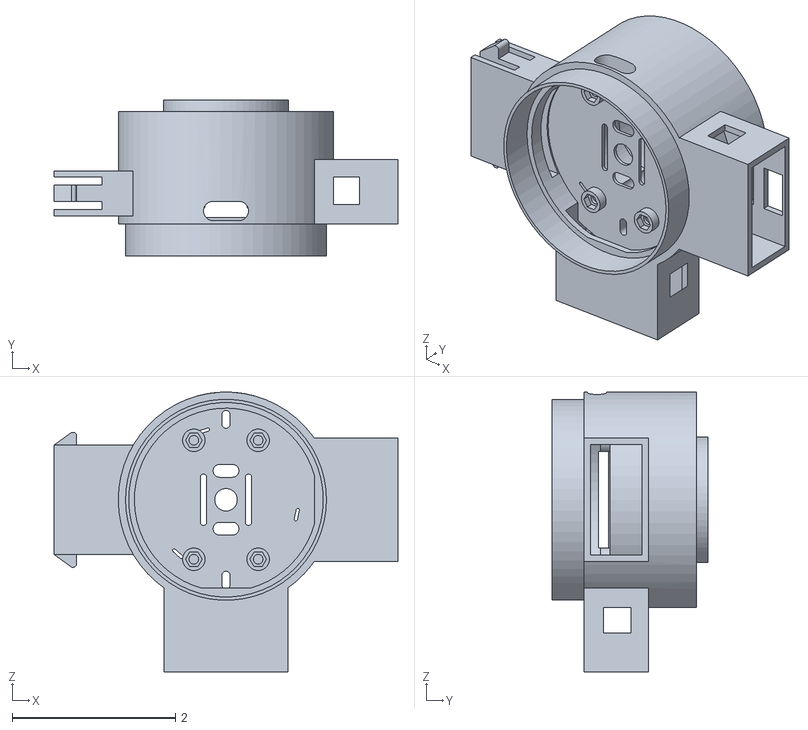
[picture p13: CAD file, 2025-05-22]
CAD_Files/inches/Base Segment (in).stl
4.21 x 1.91 x 3.42

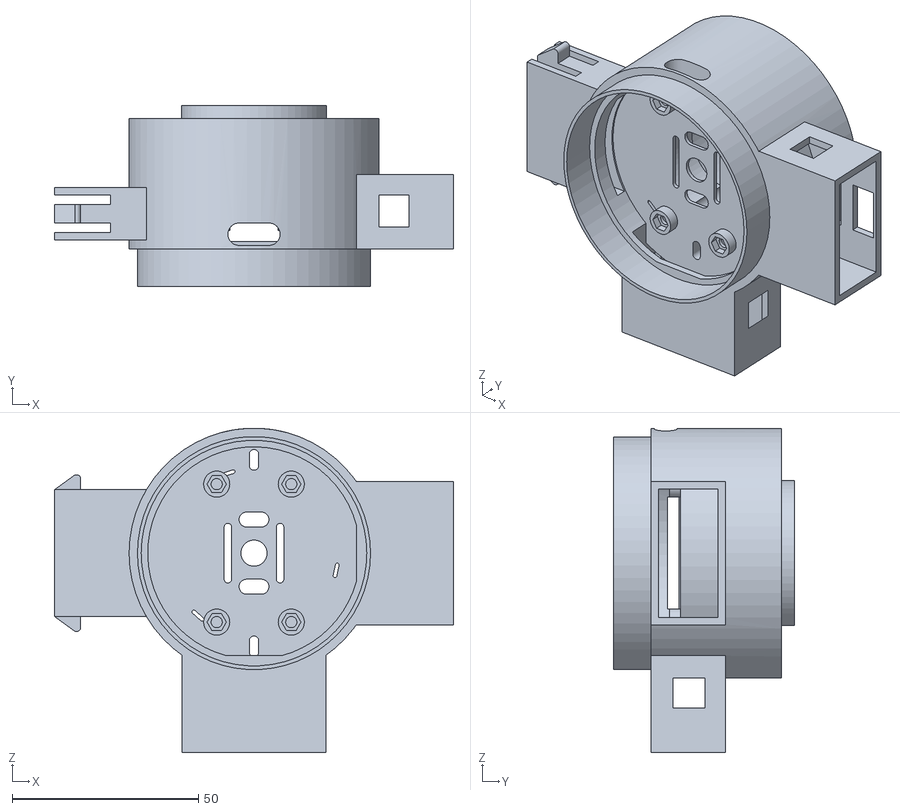
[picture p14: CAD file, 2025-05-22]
CAD_Files/millimeters/Base Segment (mm).stl
107.0 x 48.5 x 87.0

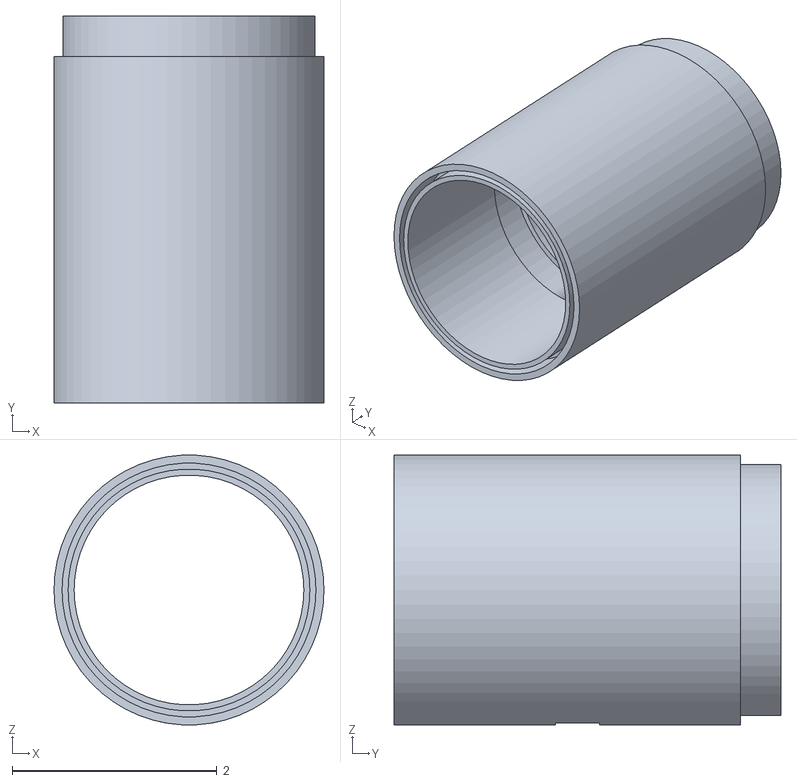
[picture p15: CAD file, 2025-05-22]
CAD_Files/inches/Lagoon Segment (in).stl
2.64 x 3.78 x 2.63

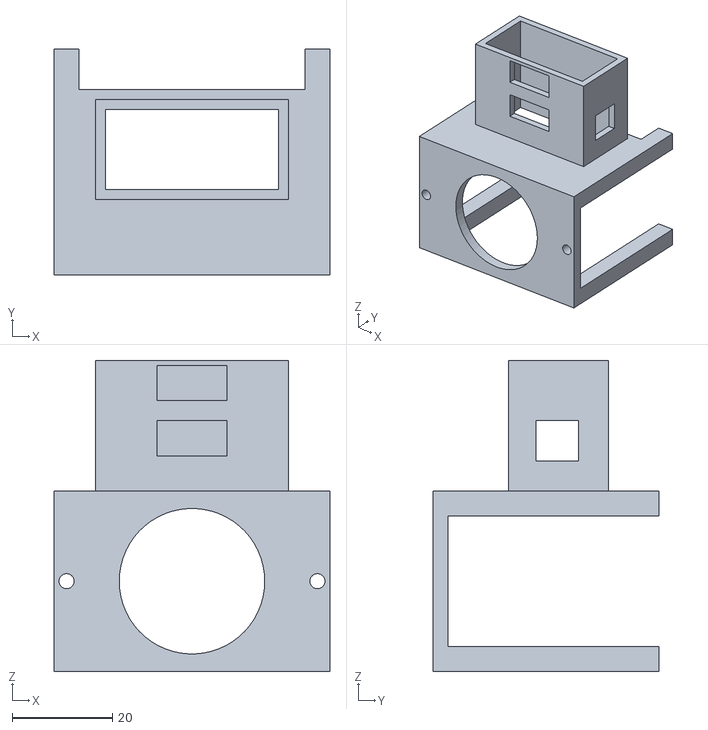
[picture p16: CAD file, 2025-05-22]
CAD_Files/millimeters/Pump Holder (mm).stl
55.0 x 45.0 x 62.0

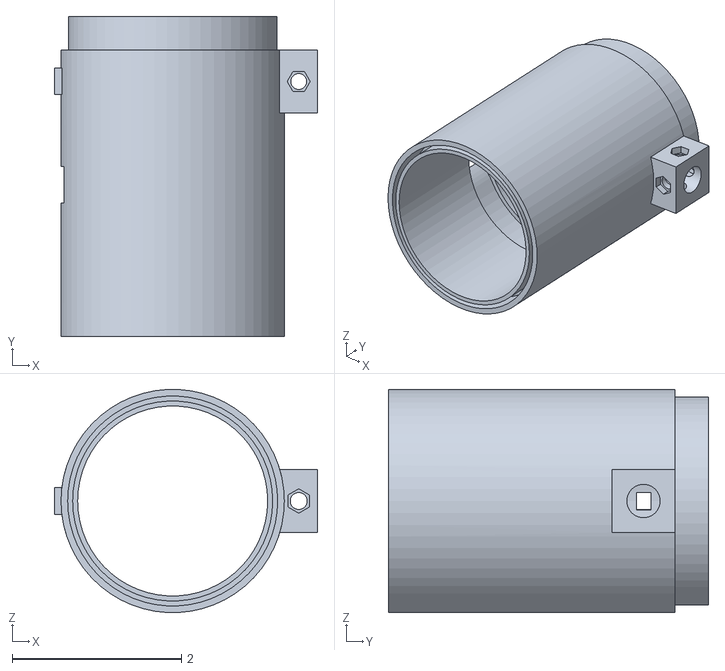
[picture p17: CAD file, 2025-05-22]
CAD_Files/inches/Turbidostat Segment (in).stl
3.11 x 3.78 x 2.63

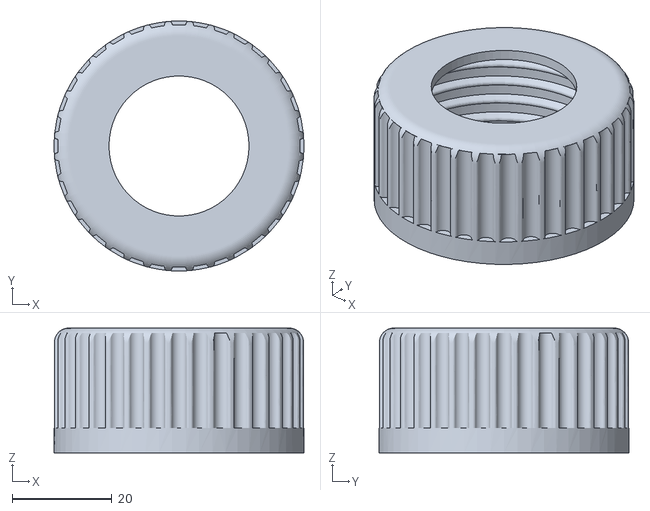
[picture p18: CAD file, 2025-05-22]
CAD_Files/millimeters/Custom Cap for 100ml bottle (mm).stl
50.0 x 49.9 x 25.0

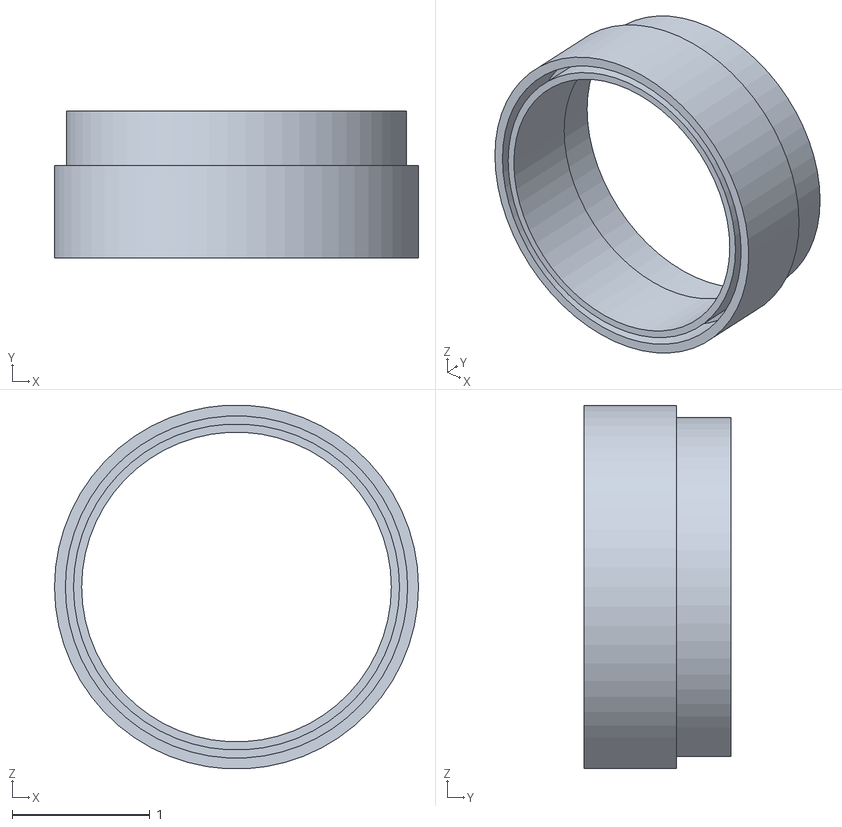
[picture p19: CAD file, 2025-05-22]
CAD_Files/inches/Intermediate Base Segment (in).stl
2.64 x 1.06 x 2.63

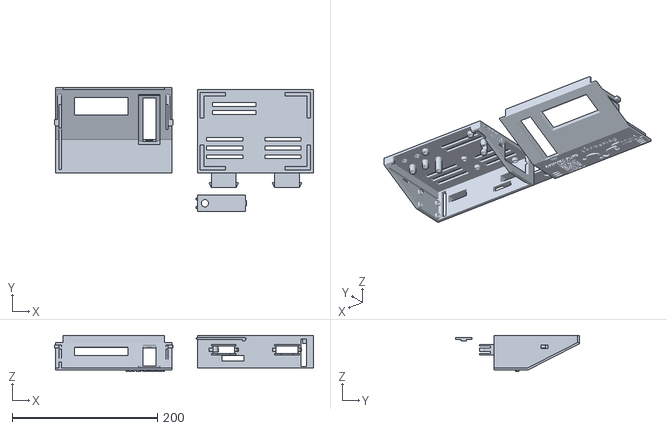
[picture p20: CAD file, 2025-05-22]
CAD_Files/millimeters/Control Unit with Lid (mm).stl
356.5 x 171.0 x 50.0

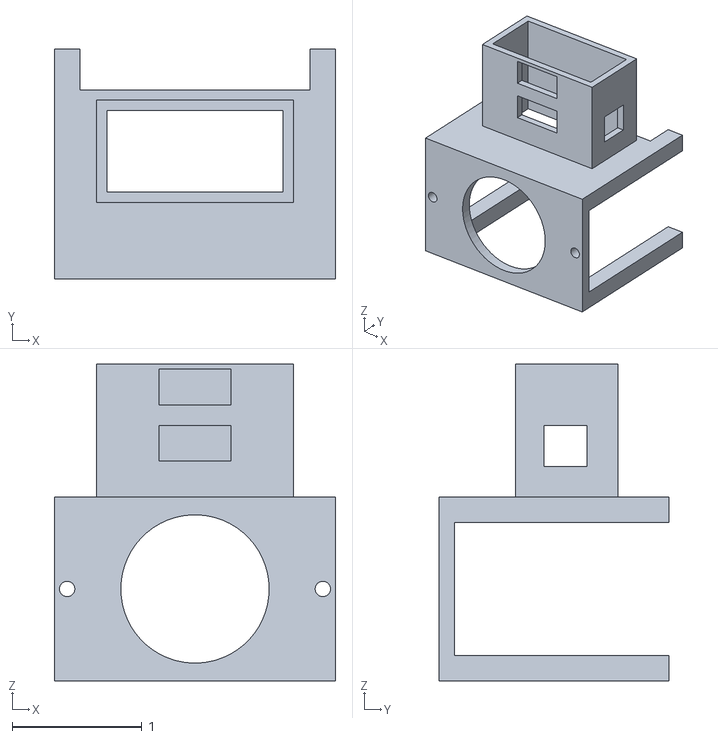
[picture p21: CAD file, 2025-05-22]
CAD_Files/inches/Pump Holder (in).stl
2.17 x 1.77 x 2.44

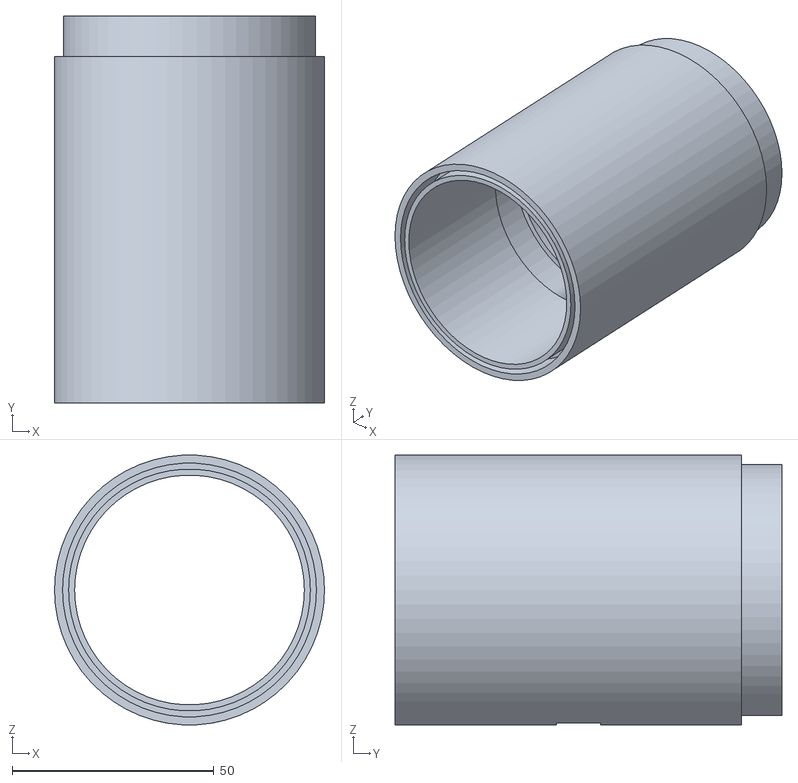
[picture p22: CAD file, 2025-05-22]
CAD_Files/millimeters/Lagoon Segment (mm).stl
67.0 x 96.0 x 66.9

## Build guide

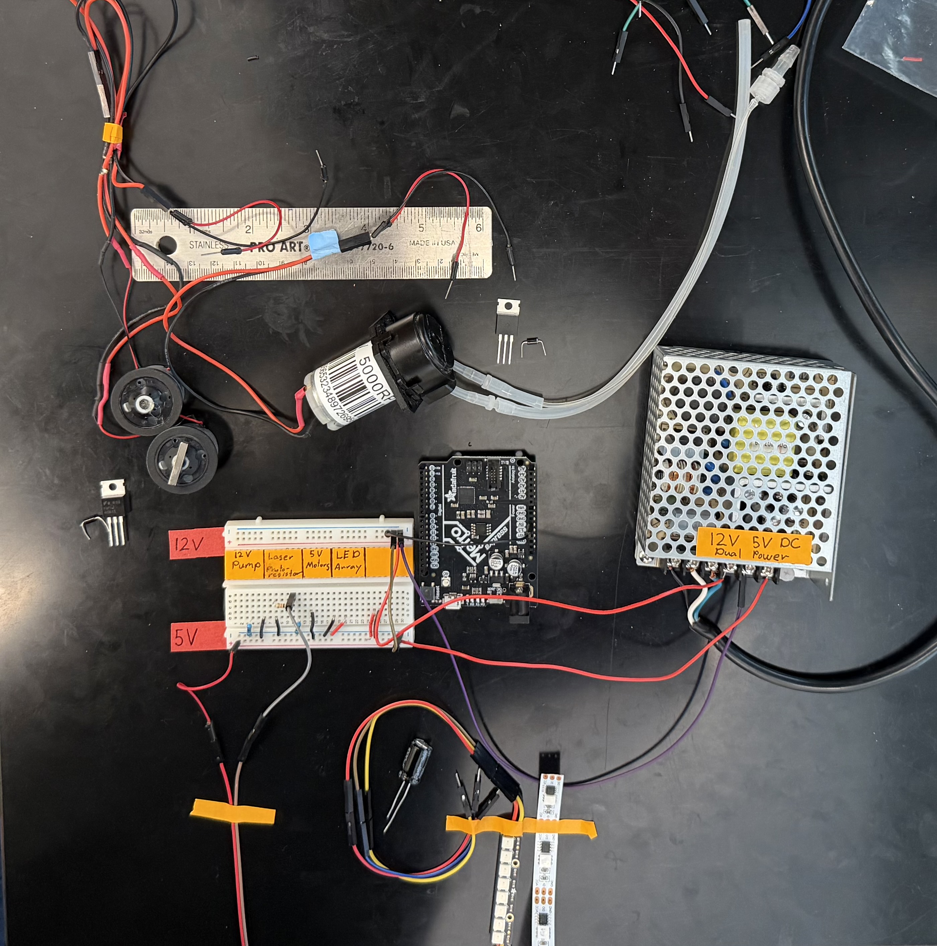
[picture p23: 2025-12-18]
Images/Prototype assembly [Step 3] .jpeg

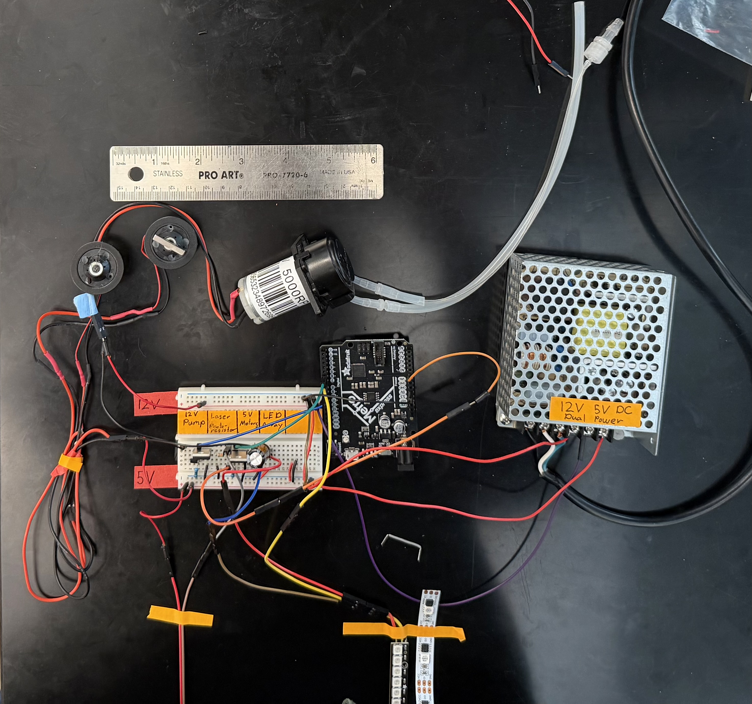
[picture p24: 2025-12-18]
Images/Prototype assembly [Step 6] .jpeg

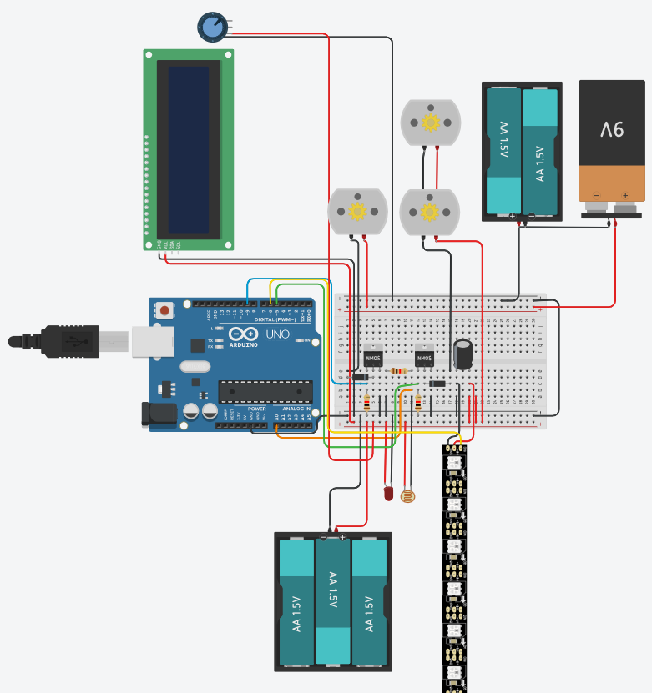
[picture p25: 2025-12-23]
Images/Prototype assembly [Step 6] - Schematic.png

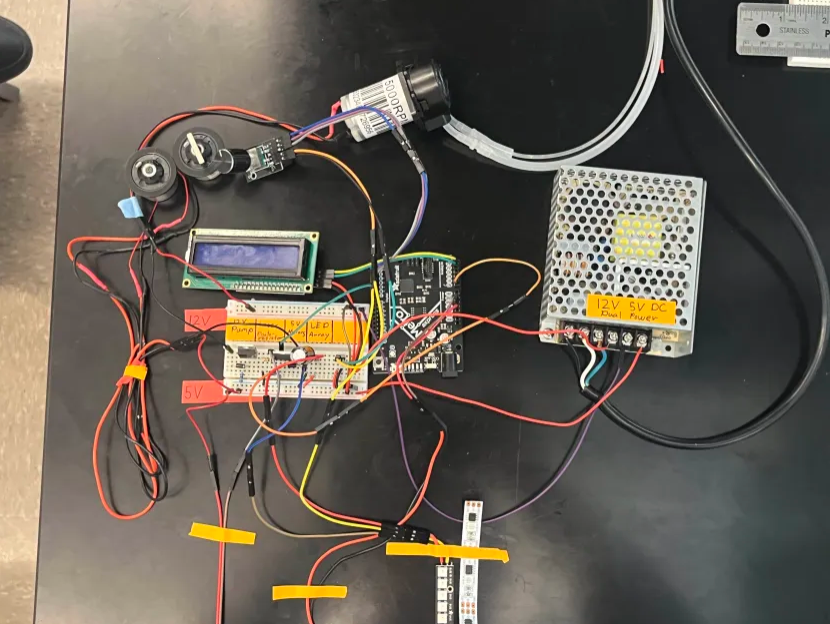
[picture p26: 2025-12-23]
Images/Prototype assembly [Step 7].png

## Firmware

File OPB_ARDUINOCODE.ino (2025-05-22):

// Import libraries
#include <Wire.h>
#include <LiquidCrystal_I2C.h>
#include <Adafruit_NeoPixel.h>

#include <SPI.h>
#include <SD.h>

#define ENCA 2
#define ENCB 3
#define DEBOUNCE_DELAY 50

// Mid log Set point Variables
// int setpoint = x; <-Replace x with the midlog value you find, it should be in the range of 0-1023
int setpoint = 800;                         // This variable is set to the value of the photoresistor when the bacteria should hit mid log growth. When the photoresistor reading matches this set point the pump will turn on and move media.
bool setpointhit = false;                   // This is a boolean that tells the code when the set point has been hit we set this to false when the code starts
unsigned long previousintervalsensor = 0;   // Similar to the variable for the pump function, this variable is the time when the sensor was last read, and is initally set to 0.
unsigned long setpointdelay = 5000;         // This variable determines the time between when the program checks if the sensor value is equivelent to the set point. The time is in milliseconds so here we have a 10 second delay.

// LCD Screen Menus
enum MenuState {MAIN_MENU, SUBMENUSTARTBACK, SUBRUNPACESD, SUBMENUTIME, SUBSETTIME, SUBPACEOFF, SUBMENUCHANGELEDS, SUBCHANGELEDS, SUBCALIBRATION, SUBSTOPCLEANING, SUBSTOPCLEANINGPROMPT};
MenuState currentMenu = MAIN_MENU;
LiquidCrystal_I2C lcd(0x27, 16, 2);

volatile int time = 0;

// Rotary encoder variables
volatile int counter = 0;
int buttonState = 0;
int lastButtonState = 0;
const int buttonPin = 4;
unsigned long lastDebounceTime = 0;
bool buttonPressed = false;

const int stir1 = 5;  // Assigns the stirmotors to pin 5 on the microcontroller

// Variables for Peristaltic Pump function
const int pump = 9;                         // Assigns the pump to pin 9
unsigned long previousintervalpump = 0;     // This variable is set to 0 in our loop function it is set to time when the pump was last turned on                                    
unsigned long pumponinterval = 1000;        // Controls how long the runs once it is turned on. The time is in milliseconds in our case the pump is on for 1 second or 1000 milliseconds
unsigned long currenttime = 0;              // This variable represents the current time of the system we set it to 0 to start

// Variables for Optical Density Measurements
const int sensor1pin = A0;                 // This sets the pin for the photoresistor as A0 on the microcotroller  
int sensor1;                               // This initilizes a variable to store the value of the photoresistor reading
unsigned long sensordelay = 1000;          // This variable determines the time between when the voltage across the photoresistor is read. ie the time between sensor readings

// Variables for Averaging Function        // To combat potnetial noise in the system, our code averages the sensor values it reads
int counterSensor = 0;                     // This variable counts the amount of times a sensor reading is taken
int sum = 0;                               // This variable stores the sum of the sensor reading values
int average = 0;                           // This variable stores the computed average

// Variables for NeoPixel LEDs
const int LEDpin = 6;
int numleds = 8;
int numledsuv = 12;
Adafruit_NeoPixel pixels = Adafruit_NeoPixel(numleds,LEDpin, NEO_GRB + NEO_KHZ800);
Adafruit_NeoPixel pixelsuv = Adafruit_NeoPixel(numledsuv, LEDpin, NEO_GRB + NEO_KHZ800);
uint32_t WHITE = pixels.Color(255,255,255);
uint32_t RED = pixels.Color(255,0,0);
uint32_t GREEN = pixels.Color(0,255,0);

// Variables for determining states for the menu values
bool runsystem = false;
bool runsystemsd = false;
bool settime = false;
bool paceoff = false;
bool runcalibration = false;
bool turnred = false;
bool turngreen = false;
bool turnuv = false;
bool turnblack = false;
bool stopcleaning = true;

// Variables for the cleaning function
unsigned long currenttimeclean = 0;
unsigned long timewhenclicked = 0;

//Function Declarations                   // Instead of including all of our code in one void loop function we seperated it into multiple different functions to allow for easier interpretation and editing.
void stirmotors();                        // This function runs the stir motors
void runsensors();                        // This function tells the arduino to collect data from the photoresistor
void checksetpoint();                     // This function checks to see if the sensor value has hit the set point
void LEDs();
void turnPaceOff();


void setup() {
  lcd.init();
  lcd.backlight();

  pinMode(ENCA, INPUT_PULLUP);
  pinMode(ENCB, INPUT_PULLUP);
  attachInterrupt(digitalPinToInterrupt(ENCA), read_encoder, CHANGE);
  attachInterrupt(digitalPinToInterrupt(ENCB), read_encoder, CHANGE);
  pinMode(buttonPin, INPUT_PULLUP);

  MenuDisplay();  // Display the initial menu correctly

  //Stirmotor Function
  pinMode(stir1, OUTPUT);                // Sets the stirmotor pin to an output, so the microcontroller can control when and how fast the stir motors spin.
 
  //Pump Function
  pinMode(pump, OUTPUT);                // Sets the pump pin as an output, this allows the microcontroller to control for how long and how fast the pump is moving liquid.
 
  pixelsuv.begin();
  pixelsuv.clear();
  pixelsuv.show();
  pixels.begin();
  pixels.clear();
  pixels.show();
 
  // Set up for LEDs
 
  Serial.begin(115200);
}

void loop() {

  // Run PACE
  if (runsystem == true) {
    currenttime = millis();             // This uses the millis(); function to set the variable currenttime to the currenttime
    stirmotors();                       // Calls the function stirmotors
    runsensors();                       // Calls the function runsensors
    checksetpoint();                    // Calls the function checksetpoint    
    LEDs();
  }

  // Turn off the system
  if (runsystem == false && runcalibration == false && settime == false && stopcleaning == true) {
    analogWrite(stir1,0);
    analogWrite(pump,0);
  }
  
  // Run the set time function for cleaning
  if (settime == true) {
    runpumptime();
  }

  // Run the calibration function 
  if (runcalibration == true) {
    currenttime = millis();
    stirmotors();
    runsensors();
  }

  // Turn the RGB LEDs red
  if (turnred == true) {
    red();
  }

  // Turn the RGB LEDs green
  if (turngreen == true) {
    green();
  }

  // Turn only the UV LEDs on
  if (turnuv == true) {
    uv();
  }
 
  // Turn off the LEDs
  if (turnblack == true) {
    black();
  }

  // Update menu display
  MenuDisplay();

  // Handle button press
  if (buttonPressed) {
    handleButtonPress();
    buttonPressed = false;  // Reset the button press flag
  }

  // Rotary encoder output
  static int lastCounter = 0;
  if(counter != lastCounter) {
    //Serial.println(counter);
    lastCounter = counter;
  }
 
  // Debounce button press
  int reading = digitalRead(buttonPin);
  if (reading != lastButtonState) {
    lastDebounceTime = millis();
  }
  if ((millis() - lastDebounceTime) > DEBOUNCE_DELAY) {
    if (reading != buttonState) {
      buttonState = reading;
      if (buttonState == LOW) {
        buttonPressed = true;
      }
    }
  }
  lastButtonState = reading;
}

// Pump Function
void runpump(){
 analogWrite(pump, 255);     // This is the maximum output of an analog pin and essentially tells the pump to run at full speed. We decided to keep the analog function here instead of using digital write to allow others to easily change the pump speed.        
}

// Pump function for cleaning as certain amount of time in minutes
void runpumptime(){ 
 currenttimeclean = millis();
 if ((currenttimeclean - timewhenclicked < (time*60000)))  {
 analogWrite(pump, 255);
 }
 else if (currenttimeclean - timewhenclicked > (time*60000)){
 analogWrite(pump, 0);

 settime = false;  
 }            
 stopcleaning = true;
 
}

// Stop running the pump
void stopclean(){
  analogWrite(pump,0);
}

// set point function
void checksetpoint() {
if(average <= setpoint && !setpointhit) {     // If the sensor value is less then or equal to the setpoint and the boolean setpointhit then execute the code within the {}
  setpointhit = true;                         // Sets the boolean named setpointhit to true, telling the code that the optical density of mid log growth has been achieved
  previousintervalpump = currenttime;         // Resets the interval variable to ensure that it represents the time when the pump was last turned on  
  Serial.println(F("Pump is on"));
  }
  if(setpointhit) {                                                     // If the setpointhit boolean is set to true then execute the code in the {}
    if(currenttime - previousintervalpump < pumponinterval){            // If the current time minus the time when the pump was last on is less then the interval run the pump
     runpump();                                                         // This calls the run pump function
    } else if (currenttime - previousintervalpump >= pumponinterval){   // Otherwise if the current time minus the last time the pump was on is greater then or equal to the amount of time the pump should be on then execute what is in the {}
     analogWrite(pump, 0);                                              // This is the lowest possible value of the analogWrite function and subsequently turns the pump off
    }
 
    if(currenttime - previousintervalpump >= setpointdelay) {           // Asks if the delay or the time between when the program should check the sensor value has been met if that time has been met then execute what is in the {}
      setpointhit = false;                                              // If the time has elapsed, in this case 10 seconds then we no longer know if the setpoint has been hit so we set the variable to false so the program checks the to see if it has been hit again
    }
  } else {
    analogWrite(pump,0);                                                
  }
}




// Stirmotor Function
void stirmotors(){
 analogWrite(stir1, 70);                                     // Powers the stir motors with the specified voltage, ensuring the subsequent vortex does not interfere with OD measurements
}
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

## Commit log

2025-05-22 Calibration Experiments files
2025-05-22 Create millimeters
2025-12-18 Add image to README for prototype assembly step 1
2025-12-23 Changes to be committed: Arranged image files into 'Images' folder: renamed: Parts connected to microcontroller [not shown in assembly].jpeg -> Images/Parts connected to microcontroller [not shown in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
